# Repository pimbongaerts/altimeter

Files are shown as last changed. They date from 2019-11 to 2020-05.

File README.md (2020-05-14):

# Altimeter_v2

Intervalometer with serial interface based on Mega2560 MCU

*Current application:*

* Intervalometer for photogrammetry surveys (triggering a Canon 5DsR DSLR every second)
* Real-time sensor feedback underwater (through attached OLED display):
  * Levelling and altitude (through 2 x altimeters: [BlueRobotics Ping Sonar](https://bluerobotics.com/store/sensors-sonars-cameras/sonar/ping-sonar-r2-rp/))
  * Read-out USBL communications (through [BluePrint Subsea X150 USBL](https://www.blueprintsubsea.com/pages/product.php?PN=BP00795))
  * Depth and "bottom-depth" based on altitude (through [BlueRobotics Depth Sensor](https://bluerobotics.com/store/sensors-sonars-cameras/sensors/bar30-sensor-r1/))
  * Stopwatch & intervalometer count (triggered by Remora remote)
* Logging synchronized sensor data on SD card

*Features:*

* Real-time clock (RTC) for timekeeping
* SD-card reader to log sensor data
* 4-Channel Optocoupler to trigger camera(s)
* Step-down regulator to run board & DSLR camera off external battery (e.g. from dive propulsion vehicle)
* Supports I2C (3.3V or 5V logic), UART and RS232 sensors
* Connectors for remote controller & I2C or SPI display
* Headers to connect with [Robotdyn MCU-PRO Mega 2560 board](https://robotdyn.com/mcu-pro-mega-2560-atmega2560-16au-usb-ch340c-with-pinheaders-2-lines-pinheaders-pitch-0-1.html), which can be programmed using Arduino IDE
* Fits inside [BlueRobotics 2" watertight enclosure](https://bluerobotics.com/product-category/watertight-enclosures/) (see image below)

## Schematic

[PDF Schematic](altimeter_v2_schematic.pdf)

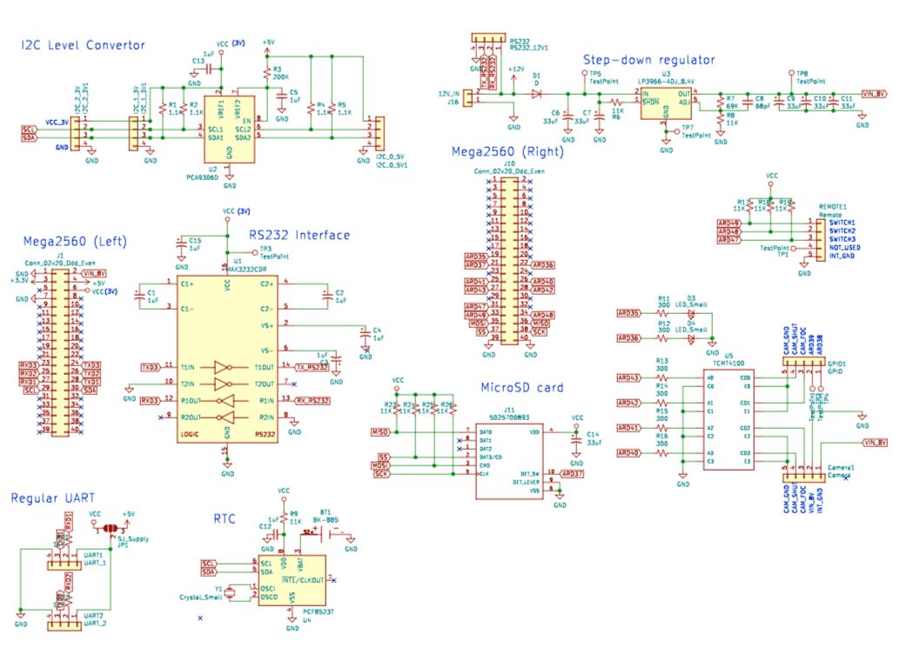
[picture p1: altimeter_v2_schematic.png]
altimeter_photo


* Note: LP3966 on schematic replaced with [TL1963AKTTRG3](https://www.digikey.com/product-detail/en/texas-instruments/TL1963AKTTRG3/296-35958-1-ND/4135050) (has the same footprint)

## Arduino code

[Arduino code](altimeter_v2.ino) (some features are currently commented out)

## PCB Design

[KiCad PCB file](altimeter_v2.kicad_pcb) / [Bill of materials](altimeter_v2_bill.csv)

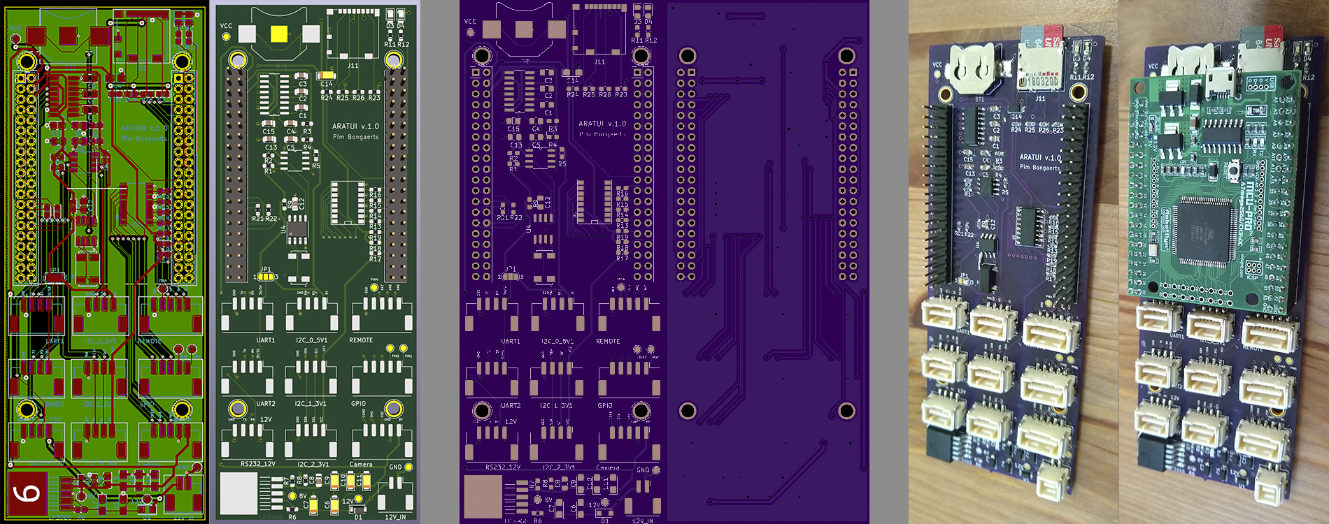
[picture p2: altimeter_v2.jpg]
altimeter_photo


* Note: footprint of the [XC1195CT-ND Crystal](https://www.digikey.com/product-detail/en/ecs-inc/ECS-327-12-5-17X-TR/XC1195CT-ND/827659) turned out to be incorrect, but could easily remedied with direct bridge to RTC pin

## Underwater housing

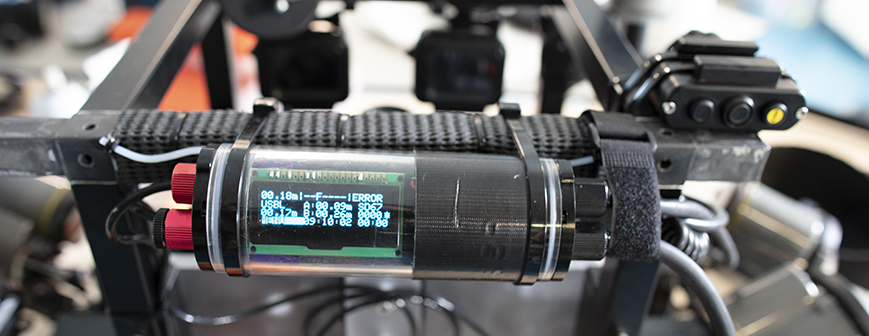
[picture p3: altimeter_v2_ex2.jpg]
altimeter_photo


Image shows board installed in a [BlueRobotics 2" watertight enclosure](https://bluerobotics.com/product-category/watertight-enclosures/), and with a 20x4 OLED display connected. On the left side, there are penetrators for an on/off switch, a [BlueRobotics Depth Sensor](https://bluerobotics.com/store/sensors-sonars-cameras/sensors/bar30-sensor-r1/), and 2 x [BlueRobotics Ping Sonar](https://bluerobotics.com/store/sensors-sonars-cameras/sonar/ping-sonar-r2-rp/) (although on the photo only one connected, hence the "error" on the top-right of the display). On the right side, there is an Ikelite connector to connect with the camera (power and trigger), another Ikelite connector for the 3-button remote (Remora), a penetrator for a cable connecting with the Dive-Xtras Piranha DPV battery, and a penetrator for the cable connecting with the [BluePrint Subsea X150 USBL](https://www.blueprintsubsea.com/pages/product.php?PN=BP00795).

## Final notes

Acknowledging John Atkins for all the design advice! Currently working on next iteration with SAMD51 integrated on the board (no external controller board required).

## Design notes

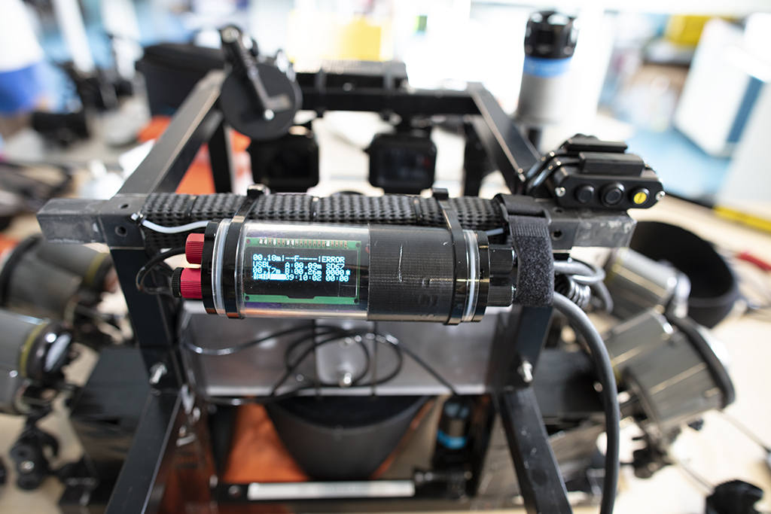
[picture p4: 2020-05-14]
altimeter_v2_ex1.jpg

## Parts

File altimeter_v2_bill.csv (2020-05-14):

BT1 | BK-885 | BAT_BK-885 | 3.17mm
C1 | 1uF | Capacitor_SMD:C_0805_2012Metric_Pad1.15x1.40mm_HandSolder | ~
C12 | 1uF | Capacitor_SMD:C_0805_2012Metric_Pad1.15x1.40mm_HandSolder | ~
C13 | 1uF | Capacitor_SMD:C_0805_2012Metric_Pad1.15x1.40mm_HandSolder | ~
C15 | 1uF | Capacitor_SMD:C_0805_2012Metric_Pad1.15x1.40mm_HandSolder | ~
C2 | 1uF | Capacitor_SMD:C_0805_2012Metric_Pad1.15x1.40mm_HandSolder | ~
C3 | 1uF | Capacitor_SMD:C_0805_2012Metric_Pad1.15x1.40mm_HandSolder | ~
C4 | 1uF | Capacitor_SMD:C_0805_2012Metric_Pad1.15x1.40mm_HandSolder | ~
C5 | 1uF | Capacitor_SMD:C_0805_2012Metric_Pad1.15x1.40mm_HandSolder | ~
C8 | 68pF | Capacitor_SMD:C_0805_2012Metric_Pad1.15x1.40mm_HandSolder | ~
C10 | 33uF | Capacitor_Tantalum_SMD:CP_EIA-3216-10_Kemet-I_Pad1.58x1.35mm_HandSolder | ~
C11 | 33uF | Capacitor_Tantalum_SMD:CP_EIA-3216-10_Kemet-I_Pad1.58x1.35mm_HandSolder | ~
C14 | 33uF | Capacitor_Tantalum_SMD:CP_EIA-3216-10_Kemet-I_Pad1.58x1.35mm_HandSolder | ~
C6 | 33uF | Capacitor_Tantalum_SMD:CP_EIA-3216-10_Kemet-I_Pad1.58x1.35mm_HandSolder | ~
C7 | 33uF | Capacitor_Tantalum_SMD:CP_EIA-3216-10_Kemet-I_Pad1.58x1.35mm_HandSolder | ~
C9 | 33uF | Capacitor_Tantalum_SMD:CP_EIA-3216-10_Kemet-I_Pad1.58x1.35mm_HandSolder | ~
J11 | 5025700893 | Connector_Card:microSD_HC_Molex_104031-0811 | Molex
J16 | 12V_IN | Connector_Molex:Molex_CLIK-Mate_502382-0270_1x02-1MP_P1.25mm_Vertical | ~
J17 | 12V_OUT | Connector_Molex:Molex_CLIK-Mate_502382-0270_1x02-1MP_P1.25mm_Vertical | ~
J9 | RS232_USBL | Connector_Molex:Molex_CLIK-Mate_502382-0270_1x02-1MP_P1.25mm_Vertical | ~
J3 | UART_1 | Connector_Molex:Molex_CLIK-Mate_502443-0470_1x04-1MP_P2.00mm_Vertical | ~
J4 | UART_2 | Connector_Molex:Molex_CLIK-Mate_502443-0470_1x04-1MP_P2.00mm_Vertical | ~
J5 | I2C_0_5V | Connector_Molex:Molex_CLIK-Mate_502443-0470_1x04-1MP_P2.00mm_Vertical | ~
J6 | I2C_1_3V | Connector_Molex:Molex_CLIK-Mate_502443-0470_1x04-1MP_P2.00mm_Vertical | ~
J8 | I2C_2_3V | Connector_Molex:Molex_CLIK-Mate_502443-0470_1x04-1MP_P2.00mm_Vertical | ~
J13 | GPIO | Connector_Molex:Molex_CLIK-Mate_502443-0570_1x05-1MP_P2.00mm_Vertical | ~
J14 | Cam1 | Connector_Molex:Molex_CLIK-Mate_502443-0570_1x05-1MP_P2.00mm_Vertical | ~
J15 | Remote | Connector_Molex:Molex_CLIK-Mate_502443-0570_1x05-1MP_P2.00mm_Vertical | ~
J1 | Conn_02x20_Odd_Even | Connector_PinHeader_2.54mm:PinHeader_2x20_P2.54mm_Vertical | ~
J10 | Conn_02x20_Odd_Even | Connector_PinHeader_2.54mm:PinHeader_2x20_P2.54mm_Vertical | ~
D1 | D | Diode_SMD:D_SOD-123F | ~
Y1 | Crystal_Small | ECS-.327-12:XTAL_ECS-.327-12.5-17X-TR | ~
JP1 | SJ_Supply | Jumper:SolderJumper-3_P1.3mm_Open_RoundedPad1.0x1.5mm_NumberLabels | ~
D3 | LED_Small | LED_SMD:LED_0805_2012Metric_Pad1.15x1.40mm_HandSolder | ~
D4 | LED_Small | LED_SMD:LED_0805_2012Metric_Pad1.15x1.40mm_HandSolder | ~
U3 | LP3966-ADJ_8.4V | LP3966ESX-ADJ_NOPB:TO170P1435X457-5N | http://www.ti.com/lit/ds/symlink/lp3966.pdf
U1 | MAX3232CDR | MAX3232CDR:SOIC127P600X175-16N | http://www.ti.com/lit/ds/symlink/max232.pdf
U4 | PCF8523T | Package_SO:SOIC-8_3.9x4.9mm_P1.27mm | https://www.nxp.com/docs/en/data-sheet/PCF8523.pdf
U2 | PCA9306D | PCA9306D_118:SOIC127P600X175-8N | http://www.ti.com/lit/ds/symlink/pca9306.pdf
R1 | 1.1K | Resistor_SMD:R_0603_1608Metric_Pad1.05x0.95mm_HandSolder | ~
R11 | 300 | Resistor_SMD:R_0603_1608Metric_Pad1.05x0.95mm_HandSolder | ~
R12 | 300 | Resistor_SMD:R_0603_1608Metric_Pad1.05x0.95mm_HandSolder | ~
R13 | 300 | Resistor_SMD:R_0603_1608Metric_Pad1.05x0.95mm_HandSolder | ~
R14 | 300 | Resistor_SMD:R_0603_1608Metric_Pad1.05x0.95mm_HandSolder | ~
R15 | 300 | Resistor_SMD:R_0603_1608Metric_Pad1.05x0.95mm_HandSolder | ~
R16 | 300 | Resistor_SMD:R_0603_1608Metric_Pad1.05x0.95mm_HandSolder | ~
R17 | 11K | Resistor_SMD:R_0603_1608Metric_Pad1.05x0.95mm_HandSolder | ~
R18 | 11K | Resistor_SMD:R_0603_1608Metric_Pad1.05x0.95mm_HandSolder | ~
R19 | 11K | Resistor_SMD:R_0603_1608Metric_Pad1.05x0.95mm_HandSolder | ~
R2 | 1.1K | Resistor_SMD:R_0603_1608Metric_Pad1.05x0.95mm_HandSolder | ~
R21 | 11K | Resistor_SMD:R_0603_1608Metric_Pad1.05x0.95mm_HandSolder | ~
R22 | 11K | Resistor_SMD:R_0603_1608Metric_Pad1.05x0.95mm_HandSolder | ~
R23 | 11K | Resistor_SMD:R_0603_1608Metric_Pad1.05x0.95mm_HandSolder | ~
R24 | 11K | Resistor_SMD:R_0603_1608Metric_Pad1.05x0.95mm_HandSolder | ~
R25 | 11K | Resistor_SMD:R_0603_1608Metric_Pad1.05x0.95mm_HandSolder | ~
R26 | 11K | Resistor_SMD:R_0603_1608Metric_Pad1.05x0.95mm_HandSolder | ~
R3 | 200K | Resistor_SMD:R_0603_1608Metric_Pad1.05x0.95mm_HandSolder | ~
R4 | 1.1K | Resistor_SMD:R_0603_1608Metric_Pad1.05x0.95mm_HandSolder | ~
R5 | 1.1K | Resistor_SMD:R_0603_1608Metric_Pad1.05x0.95mm_HandSolder | ~
R6 | 11K | Resistor_SMD:R_0603_1608Metric_Pad1.05x0.95mm_HandSolder | ~
R7 | 69K | Resistor_SMD:R_0603_1608Metric_Pad1.05x0.95mm_HandSolder | ~
R8 | 11K | Resistor_SMD:R_0603_1608Metric_Pad1.05x0.95mm_HandSolder | ~
R9 | 11K | Resistor_SMD:R_0603_1608Metric_Pad1.05x0.95mm_HandSolder | ~
U5 | TCMT4100 | TCMT4100:SOP-16

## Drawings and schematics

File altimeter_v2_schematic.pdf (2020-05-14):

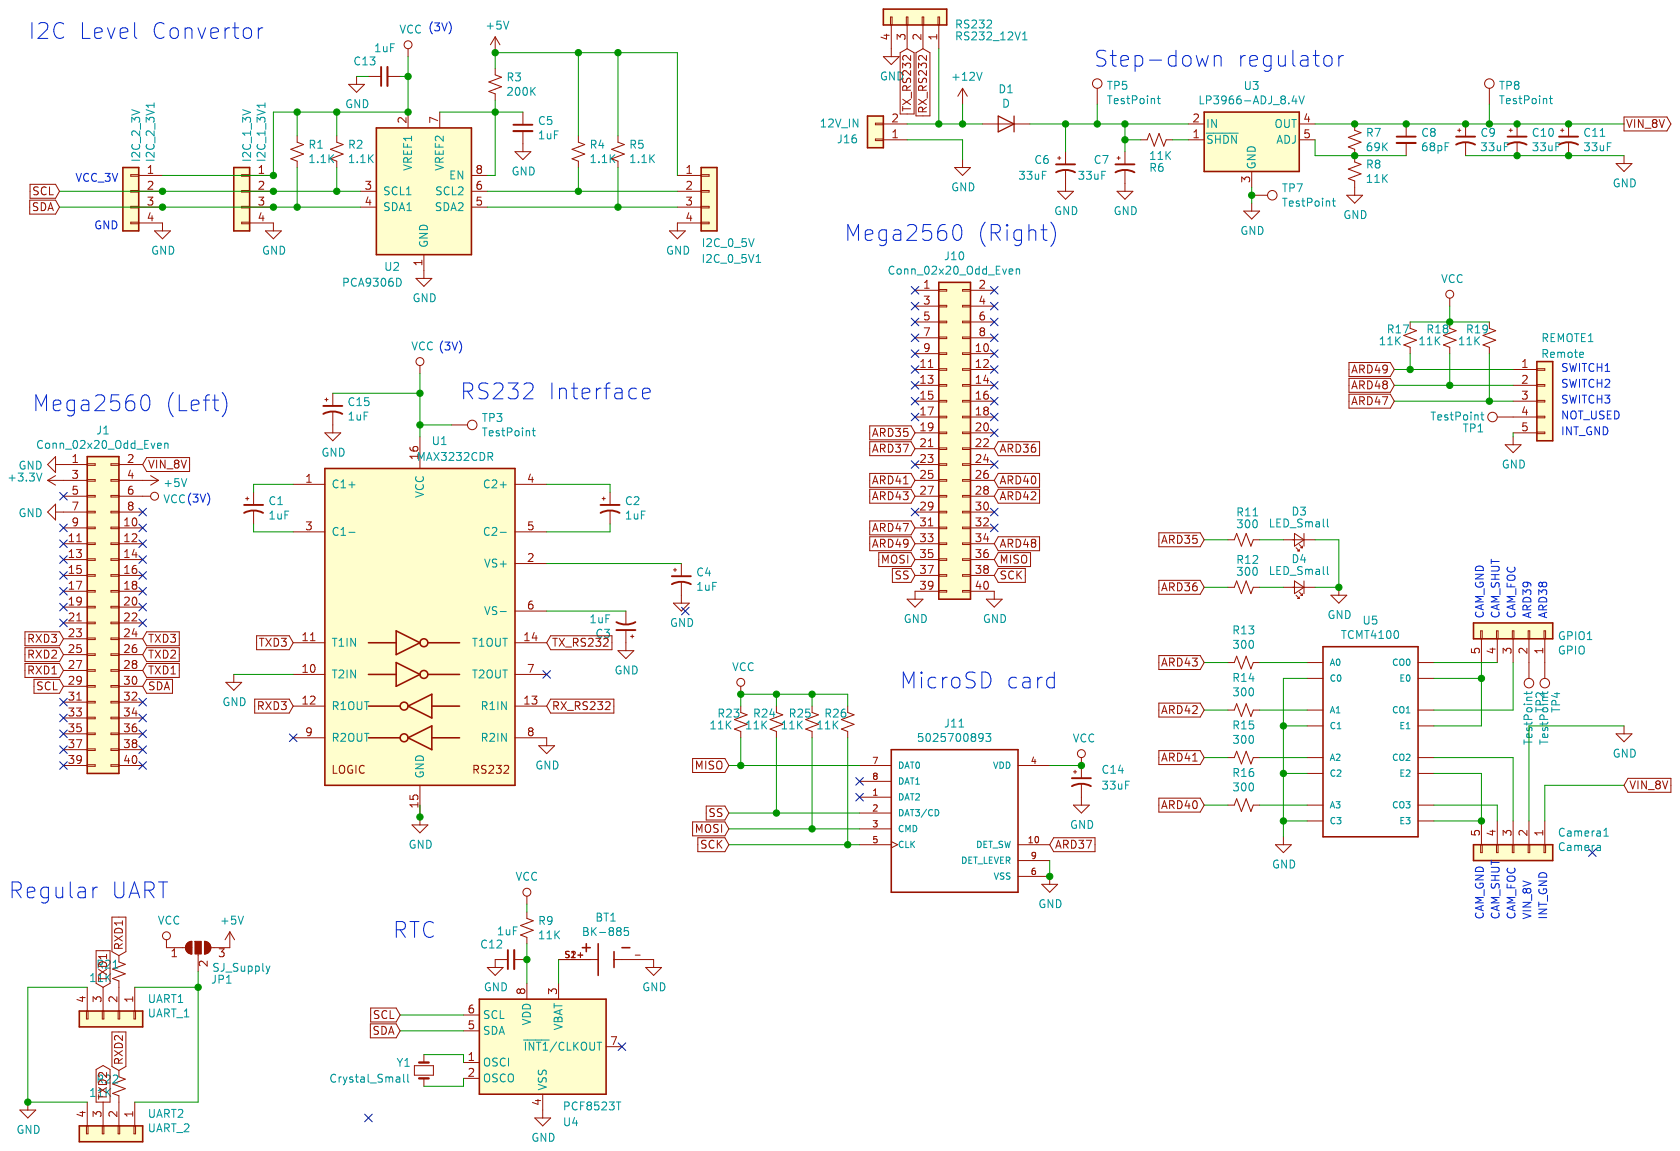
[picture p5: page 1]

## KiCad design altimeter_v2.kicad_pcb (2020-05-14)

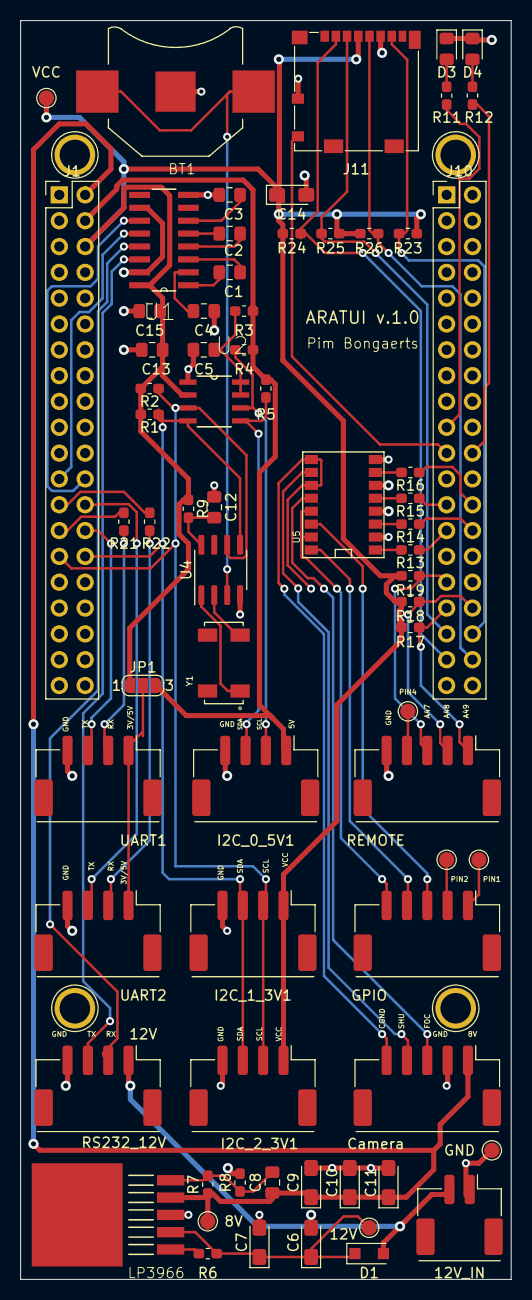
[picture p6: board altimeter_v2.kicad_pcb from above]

Board: 2 copper layers, 48.3 x 123.8 mm, 70 parts (0 on the bottom side), 63 nets.

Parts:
8V, 12V: TestPoint; TestPoint_Pad_D1.5mm
12V_IN: 12V_IN; Molex_CLIK-Mate_502443-0270_1x02-1MP_P2.00mm_Vertical
BT1: BK-885; BAT_BK-885
C1, C2, C3, C4, C5, C12, C13, C15: 1uF; C_0805_2012Metric_Pad1.15x1.40mm_HandSolder
C6, C7, C9, C10, C11, C14: 33uF; CP_EIA-3216-10_Kemet-I_Pad1.58x1.35mm_HandSolder
C8: 68pF; C_0805_2012Metric_Pad1.15x1.40mm_HandSolder
Camera: Camera; Molex_CLIK-Mate_502443-0570_1x05-1MP_P2.00mm_Vertical
D1: D; D_SOD-123F
D3, D4: LED_Small; LED_0805_2012Metric_Pad1.15x1.40mm_HandSolder
GND: TestPoint; TestPoint_Pad_D1.5mm
GPIO: GPIO; Molex_CLIK-Mate_502443-0570_1x05-1MP_P2.00mm_Vertical
I2C_0_5V1: I2C_0_5V; Molex_CLIK-Mate_502443-0470_1x04-1MP_P2.00mm_Vertical
I2C_1_3V1: I2C_1_3V; Molex_CLIK-Mate_502443-0470_1x04-1MP_P2.00mm_Vertical
I2C_2_3V1: I2C_2_3V; Molex_CLIK-Mate_502443-0470_1x04-1MP_P2.00mm_Vertical
J1, J10: Conn_02x20_Odd_Even; PinHeader_2x20_P2.54mm_Vertical
J11: 5025700893; microSD_HC_Molex_104031-0811
JP1: SJ_Supply; SolderJumper-3_P1.3mm_Open_RoundedPad1.0x1.5mm_NumberLabels
LP3966: LP3966-ADJ_8.4V; TO170P1435X457-5N
PIN1, PIN2, PIN4: TestPoint; TestPoint_Pad_D1.5mm
R1, R2, R4, R5: 1.1K; R_0603_1608Metric_Pad1.05x0.95mm_HandSolder
R3: 200K; R_0603_1608Metric_Pad1.05x0.95mm_HandSolder
R6, R8, R9, R17, R18, R19, R21, R22, R23, R24, R25, R26: 11K; R_0603_1608Metric_Pad1.05x0.95mm_HandSolder
R7: 69K; R_0603_1608Metric_Pad1.05x0.95mm_HandSolder
R11, R12, R13, R14, R15, R16: 300; R_0603_1608Metric_Pad1.05x0.95mm_HandSolder
REMOTE: Remote; Molex_CLIK-Mate_502443-0570_1x05-1MP_P2.00mm_Vertical
RS232_12V: RS232; Molex_CLIK-Mate_502443-0470_1x04-1MP_P2.00mm_Vertical
U1: MAX3232CDR; SOIC127P600X175-16N
U2: PCA9306D; SOIC127P600X175-8N
U4: PCF8523T; SOIC-8_3.9x4.9mm_P1.27mm
U5: TCMT4100; SOP-16
UART1: UART_1; Molex_CLIK-Mate_502443-0470_1x04-1MP_P2.00mm_Vertical
UART2: UART_2; Molex_CLIK-Mate_502443-0470_1x04-1MP_P2.00mm_Vertical
VCC: TestPoint; TestPoint_Pad_D1.5mm
Y1: Crystal_Small; XTAL_ECS-.327-12.5-17X-TR

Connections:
+5V: I2C_0_5V1.1, J1.4, JP1.3, R3.1, R4.1, R5.1
+12V: 12V_IN.2, D1.2, RS232_12V.1
ARD35: J10.19, R11.2
ARD36: J10.22, R12.2
ARD37: J10.21, J11.10
ARD40: J10.26, R16.2
ARD41: J10.25, R15.2
ARD42: J10.28, R14.2
ARD43: J10.27, R13.2
ARD47: J10.31, R19.1, REMOTE.3
ARD48: J10.34, R18.1, REMOTE.2
ARD49: J10.33, R17.1, REMOTE.1
GND: 12V_IN.1, BT1.-, C3.1, C4.2, C5.2, C6.2, C7.2, C9.2, C10.2, C11.2, C12.1, C13.1, C14.2, C15.2, Camera.2, D3.1, D4.1, GND.1, I2C_0_5V1.4, I2C_1_3V1.4, I2C_2_3V1.4, J1.1, J1.7, J10.39, J10.40, J11.6, J11.9, LP3966.3, R8.2, REMOTE.5, RS232_12V.4, U1.8, U1.10, U1.15, U2.1, U4.4, U5.2, U5.4, U5.6, U5.8, UART1.4, UART2.4
MISO: J10.36, J11.7, R23.1
MOSI: J10.35, J11.3, R25.1
unnamed: BT1.S1+, BT1.S2+, U4.3
unnamed: C1.1, U1.1
unnamed: C1.2, U1.3
unnamed: C2.1, U1.4
unnamed: C2.2, U1.5
unnamed: C3.2, U1.6
unnamed: C4.1, U1.2
unnamed: C5.1, R3.2, U2.7, U2.8
unnamed: 12V.1, C6.1, C7.1, D1.1, LP3966.2, R6.2
unnamed: C8.2, LP3966.5, R7.2, R8.1
unnamed: C12.2, R9.2, U4.8
unnamed: Camera.3, U5.12
unnamed: Camera.4, U5.10
unnamed: Camera.5, U5.9, U5.11
unnamed: D3.2, R11.1
unnamed: D4.2, R12.1
unnamed: GPIO.1, PIN1.1
unnamed: GPIO.2, PIN2.1
unnamed: GPIO.3, U5.14
unnamed: GPIO.4, U5.16
unnamed: GPIO.5, U5.13, U5.15
unnamed: I2C_0_5V1.2, R4.2, U2.6
unnamed: I2C_0_5V1.3, R5.2, U2.5
unnamed: JP1.2, UART1.1, UART2.1
unnamed: LP3966.1, R6.1
unnamed: R13.1, U5.1
unnamed: R14.1, U5.3
unnamed: R15.1, U5.5
unnamed: R16.1, U5.7
unnamed: R21.2, UART1.2
unnamed: R22.2, UART2.2
unnamed: PIN4.1, REMOTE.4
unnamed: U4.1, Y1.1
unnamed: U4.2, Y1.2
RXD1: J1.27, R21.1
RXD2: J1.25, R22.1
RXD3: J1.23, U1.12
RX_RS232: RS232_12V.2, U1.13
SCK: J10.38, J11.5, R26.1
SCL: I2C_1_3V1.2, I2C_2_3V1.2, J1.29, R2.2, U2.3, U4.6
SDA: I2C_1_3V1.3, I2C_2_3V1.3, J1.30, R1.2, U2.4, U4.5
SS: J10.37, J11.2, R24.1
TXD1: J1.28, UART1.3
TXD2: J1.26, UART2.3
TXD3: J1.24, U1.11
TX_RS232: RS232_12V.3, U1.14
VCC: C13.2, C14.1, C15.1, I2C_1_3V1.1, I2C_2_3V1.1, J1.6, J11.4, JP1.1, R1.1, R2.1, R9.1, R17.2, R18.2, R19.2, R23.2, R24.2, R25.2, R26.2, U1.16, U2.2, VCC.1
VIN_8V: 8V.1, C8.1, C9.1, C10.1, C11.1, Camera.1, J1.2, LP3966.4, R7.1

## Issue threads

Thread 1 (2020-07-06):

### ISSUE TITLE
Specifications: 3-button remote (Remora)

### ISSUE THREAD

**Issue by CexyNature** [pimbongaerts/altimeter#1]
Pim awesome project!
I was wondering if the 3-button remote you mention in README is a custom made product? and if these are push buttons?

> On the right side, there is an Ikelite connector to connect with the camera (power and trigger), another Ikelite connector for the 3-button remote (Remora), ...

Thanks, I look forward to the next iteration.

**Comment by pimbongaerts** [comment]
Thanks Cesar! It was a product that Backscatter used to carry (maybe produce?) - but not anymore unfortunately, and cannot really find it anywhere on the web. It has 3 push buttons and an Ikelite connector.

**Comment by CexyNature** [comment]
Thanks! It is super great idea to have a keypad with buttons. I have been looking other options like the [Blue Robotics switch](https://bluerobotics.com/store/comm-control-power/switch/switch-10-5a-r1/) or other underwater rated buttons (but these cannot be mounted in M10 holes). 

Having a keypad with three button and just one cable penetrator is an amazing setup!

Many thanks! 😃

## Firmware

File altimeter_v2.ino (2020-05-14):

/* Diving Altimeter
-----------------------------------------------------
 
Title: Aratui TEST

Description: 
-------------------------------*/
// Libraries
#include <Wire.h>                          // I2C Communication
#include <Adafruit_GFX.h>                  // Graphics for OLED
#include <Adafruit_SSD1305.h>              // OLED
#include <RTClib.h>                        // Real-time clock
#include <SPI.h>                           // SPI for SD card
#include <SD.h>                            // SD card reader
#include <MS5837.h>                        // Bar30 depth sensor
#include <ping1d.h>                        // Ping sonar / altimeter
#include <Bounce2.h>                       // Debouncing remote buttons

// Constants
#define OLED_COLS 20
#define OLED_ROWS 4
#define FLUID_DENSITY 1029
#define BUTTON_PRESS_DELAY 300
#define NOT_RESPONSIVE -999
#define NOT_RUNNING -999
#define INTERVAL 1000
#define SHUTTER_DELAY 300

// #define PIN_LED_GREEN 35               // Removed from board
// #define PIN_LED_RED 36                 // Removed from board
#define PIN_CAM_SHUTTER 40
#define PIN_CAM_FOCUS 41
#define PIN_BUTTON1 47
#define PIN_BUTTON2 48
#define PIN_BUTTON3 49
#define PIN_CHIPSELECT 53
#define OLED_RESET 70

// Global objects
File logfile;
Adafruit_SSD1305 display(OLED_RESET);
RTC_PCF8523 rtc;
MS5837 depth_sensor;
static Ping1D ping_left { Serial1 };
static Ping1D ping_right { Serial2 };

// Global objects
unsigned long stopwatch_stored_millis;
unsigned long stopwatch_start_millis;
unsigned long stopwatch_millis;
unsigned long previous_millis = 0;
int stopwatch_min = 0;
int stopwatch_sec = 0;
bool stopwatch_running = false;
bool delayed_start_stopwatch = false;
bool delayed_single_trigger_camera = false;
float ping_altitude_left = NOT_RESPONSIVE;
float ping_altitude_conf_left = NOT_RESPONSIVE;
float ping_altitude_right = NOT_RESPONSIVE;
float ping_altitude_conf_right = NOT_RESPONSIVE;
float mean_altitude = NOT_RESPONSIVE;
float bar30_depth = NOT_RESPONSIVE;
float extrapolated_depth = NOT_RESPONSIVE;
float usbl = NOT_RESPONSIVE;
int rtc_year = NOT_RESPONSIVE;
int rtc_month = NOT_RESPONSIVE;
int rtc_day = NOT_RESPONSIVE;
int rtc_hour = NOT_RESPONSIVE;
int rtc_min = NOT_RESPONSIVE;
int rtc_sec = NOT_RESPONSIVE;
unsigned long rtc_unixtime = NOT_RESPONSIVE;
int sd_file_number = NOT_RESPONSIVE;
int progress_update = -1;
int intervalometer_number = NOT_RUNNING;
int total_trigger_number = 0;
int current_menu = 0;
byte customBackslash[8] = {
  0b00000,
  0b10000,
  0b01000,
  0b00100,
  0b00010,
  0b00001,
  0b00000,
  0b00000
};

void init_pins() {
  // Initialize pins
  pinMode(PIN_BUTTON1, INPUT);
  pinMode(PIN_BUTTON2, INPUT);
  pinMode(PIN_BUTTON3, INPUT);
  pinMode(PIN_CAM_SHUTTER, OUTPUT);
  pinMode(PIN_CAM_FOCUS, OUTPUT);
}

// Initialize LCD screen
void init_oled() {
  display.begin();
  display.clearDisplay();
  display.display();
  display.setTextSize(1);
  display.setTextColor(WHITE);
  display.setCursor(0,0);
  display.println("DEEPCAT");
  display.display();
}

// Initialize Real-Time Clock
void init_rtc() {
  if (! rtc.begin()) {
    rtc_hour = NOT_RESPONSIVE;
  } else {
    // SET TIME TO CURRENT COMPUTER TIME
    // rtc.adjust(DateTime(F(__DATE__), F(__TIME__)));
    // Update current date/time
    get_rtc_time();
  }
}

void get_rtc_time() {
  DateTime now = rtc.now();
  rtc_year = now.year();
  rtc_month = now.month();
  rtc_day = now.day();
  rtc_hour = now.hour();
  rtc_min = now.minute();
  rtc_sec = now.second();
  rtc_unixtime = now.unixtime();
}

// Initialize SD card
void init_sdcard() {
  display.clearDisplay();
  pinMode(PIN_CHIPSELECT, OUTPUT);
  if (!SD.begin(PIN_CHIPSELECT)) {
    sd_file_number = NOT_RESPONSIVE;
  }
  // create a new file
  char filename[] = "ARAT0000.CSV";
  for (uint8_t i = 0; i < 10000; i++) {
    filename[4] = '0' + ((i / 1000) % 10);
    filename[5] = '0' + ((i / 100) % 10);
    filename[6] = '0' + ((i / 10) % 10);
    filename[7] = '0' + (i % 10);
    if (! SD.exists(filename)) {
      // only open a new file if it doesn't exist
      logfile = SD.open(filename, FILE_WRITE);
      sd_file_number = i;
      break;  // leave the loop!
    }
  }
  if (! logfile) {
    sd_file_number = NOT_RESPONSIVE;
  } else {
    // print logfile header
    logfile.println(F("date,time,unixtime,depth,left_altitude,left_altitude_confidence,right_altitude,right_altitude_confidence,mean_altitude,extrapolated_depth,stopwatch_time,intervalometer_no,total_trigger_number,millis"));
  }
}

void init_depth_sensor() {
  // Initialize pressure depth_sensor (true if initialization was successful)
  Wire.begin();
  while (!depth_sensor.init()) {
    delay(1000);
  }
  depth_sensor.setModel(MS5837::MS5837_30BA);
  depth_sensor.setFluidDensity(FLUID_DENSITY);
  get_bar30_depth();
}

// Obtain depth measurement
void get_bar30_depth() {
  depth_sensor.read();
  bar30_depth = depth_sensor.depth(); 
}

// Initialize left altimeter
void init_sonar_left() {
  Serial1.begin(9600);
  int attempts = 0;
  while (!ping_left.initialize()) { 
    if (attempts > 3) { break; }
    attempts++;
    delay(200);
  }
  ping_get_altitude_left();
}

// Initialize right altimeter
void init_sonar_right() {
  Serial2.begin(115200);
  int attempts = 0;
  while (!ping_right.initialize()) { 
    if (attempts > 10) { break; }
    attempts++;
    delay(500);
  }
  ping_left.set_ping_enable(true); // to remove
  ping_get_altitude_right();
}

// Initialize right altimeter
void init_usbl() {
  Serial3.begin(115200);
  if (Serial3.available() <= 0 ) {
    usbl = NOT_RESPONSIVE;
  }
}

// Obtain altitude measurement
void ping_get_altitude_left() {
    // ping_left.set_ping_enable(true);
    if (ping_left.update()) {
        ping_altitude_left = (float)ping_left.distance() / 1000;
        ping_altitude_conf_left = ping_left.confidence();
    } else {
        ping_altitude_left = NOT_RESPONSIVE;
        ping_altitude_conf_left = 0;
    }
    // ping_left.set_ping_enable(false);
}

// Obtain altitude measurement
void ping_get_altitude_right() {
    // ping_right.set_ping_enable(true);
    if (ping_right.update()) {
        ping_altitude_right = (float)ping_right.distance() / 1000;
        ping_altitude_conf_right = ping_right.confidence();
    } else {
        ping_altitude_right = NOT_RESPONSIVE;
        ping_altitude_conf_right = 0;
    }
    // ping_right.set_ping_enable(false);
}
// Obtain USBL information
void usbl_get_data() {
  if (Serial3.available() > 0) {
    usbl = 1;
  } else {
    usbl = NOT_RESPONSIVE;
  }
}

// Print depth/altitude to LCD
void oled_print_6char(float number) {
  if (number == NOT_RESPONSIVE) {
    display.print(F("-N/A- "));
  } else if (number >= 1000) {
    display.print(F("100+m "));
  } else if (number > 100) {
    display.print((int) number);
    display.print(F("m "));
  } else if (number > 10) {
    display.print(number);
    display.print(F("m"));
  } else if (number > 0) {
    display.print(F("0"));
    display.print(number);
    display.print(F("m"));
  } else if (number < 0) {
    display.print(F("-NEG- "));
  } else {
    display.print(F("ERROR "));
  }
}

// Print time to OLED
void oled_print_rtc_time(int number1, int number2, int number3) {
  if (number1 == NOT_RESPONSIVE) {
    display.print(F("-N/A-"));
  } else {
    if (number1 < 10) { display.print(F("0")); }
    display.print(number1);
    display.print(F(":"));
    if (number2 < 10) { display.print(F("0")); }
    display.print(number2);
    display.print(F(":"));
    if (number3 < 10) { display.print(F("0")); }
    display.print(number3);
  }
}

// Print time to OLED
void oled_print_time(int number1, int number2) {
  if (number1 == NOT_RESPONSIVE) {
    display.print(F("-N/A-"));
  } else {
    if (number1 < 10) { display.print(F("0")); }
    display.print(number1);
    display.print(F(":"));
    if (number2 < 10) { display.print(F("0")); }
    display.print(number2);
  }
}

// Print SD card filenumber to OLED
void oled_print_sd_card() {
  if (sd_file_number == NOT_RESPONSIVE) {
    display.print(F("NOSD"));
    return;
  } else if (sd_file_number < 10) {
    display.print(F("SD0"));
  } else if (sd_file_number < 100) {
    display.print(F("SD"));
  } else if (sd_file_number < 1000) {
    display.print(F("0"));
  }
  display.print(sd_file_number);
}

// Print photo number to OLED
void oled_print_total_trigger_number() {
  if (total_trigger_number < 10) {
    display.print(F("000"));
  } else if (total_trigger_number < 100) {
    display.print(F("00"));
  } else if (total_trigger_number < 1000) {
    display.print(F("0"));
  }
  display.print(total_trigger_number);
}

// Get mean altitude
void get_mean_altitude() {
  if ((ping_altitude_left != NOT_RESPONSIVE) && (ping_altitude_right != NOT_RESPONSIVE)) {
    mean_altitude = (ping_altitude_left + ping_altitude_right) / 2;
  } else if (ping_altitude_left != NOT_RESPONSIVE) {
    mean_altitude = ping_altitude_left;
  } else if (ping_altitude_right != NOT_RESPONSIVE) {
    mean_altitude = ping_altitude_right;
  } else {
    mean_altitude = NOT_RESPONSIVE;
  }
}

// Get extrapolated depth
void get_extrapolated_depth() {
  if (mean_altitude != NOT_RESPONSIVE) {
    extrapolated_depth = bar30_depth + mean_altitude;
  } else {
    extrapolated_depth = NOT_RESPONSIVE;
  }
}

// Get progress update character
void oled_print_progress_character() {
  display.setCursor(122, 17);
  if (intervalometer_number == NOT_RUNNING) {
    if (progress_update == 0) { 
      display.print(F("*")); 
    } else {
      display.print(F("."));
      progress_update = -1;
    }
  } else {
    if (progress_update == 0) { 
      display.print(F("|")); 
    } else if (progress_update == 1) { 
      display.print(F("/")); 
    } else if (progress_update == 2) { 
      display.print(F("-")); 
    } else {
      display.print(F("\\"));
      progress_update = -1;
    }
  }
}

// Get progress update character
void oled_print_button_character() {
  display.setCursor(122,17);
  display.print(F("B"));
  display.display();
}
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

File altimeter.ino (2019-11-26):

/* Diving Altimeter
-----------------------------------------------------
 
Title: Diving Altimeter

Description: Displays (LCD) and logs (SD card) depth 
and altitude. Designed for Arduino Uno with Adafruit
Datalogger Shield and BlueRobotics Ping & Bar30 
sensors.

-------------------------------*/
// Libraries
#include <SPI.h>
#include <SD.h>
#include <Wire.h>
#include <MS5837.h>
#include <hd44780.h>
#include <hd44780ioClass/hd44780_I2Cexp.h>
#include "RTClib.h"
#include "ping1d.h"
#include "SoftwareSerial.h"

// Constants
#define chipSelect 8
#define arduinoRxPin 9
#define arduinoTxPin 10
#define LCD_COLS 20
#define LCD_ROWS 4
#define FLUID_DENSITY 1029

// Global objects/variables
File logfile;
SoftwareSerial pingSerial = SoftwareSerial(arduinoRxPin, arduinoTxPin);
hd44780_I2Cexp lcd;
MS5837 depth_sensor;
RTC_PCF8523 rtc;
static Ping1D ping { pingSerial };

// Initialize LCD screen
void init_lcd() {
  int lcd_status;
  lcd_status = lcd.begin(LCD_COLS, LCD_ROWS);
  if(lcd_status) {
    // // non-zero status means begin() failed
    lcd_status = -lcd_status; // convert negative status value to positive number
    hd44780::fatalError(lcd_status); // error code using the onboard LED if possible & exit
  }
  // Clear screen
  lcd.clear();
}

// Initialize Real-Time Clock
void init_rtc() {
  lcd.setCursor(0, 0);
  if (! rtc.begin()) {
    lcd.print(F("Real-time clock...NO"));
  }
  // Set time to current computer time (at compile)
  rtc.adjust(DateTime(F(__DATE__), F(__TIME__)));
  lcd.print(F("Real-time clock...OK"));
}

// Initialize depth sensor
void init_depth_sensor() {
  lcd.setCursor(0, 1);
  Wire.begin();
  // Initialize pressure depth_sensor (true if initialization was successful)
  while (!depth_sensor.init()) {
    lcd.print(F("Depth sensor...   NO"));
    delay(3000);
  }
  depth_sensor.setModel(MS5837::MS5837_30BA);
  depth_sensor.setFluidDensity(FLUID_DENSITY);
  lcd.print(F("Depth sensor...   OK"));
}

// Initialize altimeter
void init_sonar() {
  pingSerial.begin(9600);
  while (!ping.initialize()) {
    lcd.print(F("Sonar...          NO"));
    delay(3000);
  }
  lcd.setCursor(0, 2);
  lcd.print(F("Sonar...          OK"));
}

// Initialize SD card
void init_sdcard() {
  lcd.setCursor(0, 3);
  pinMode(chipSelect, OUTPUT);
  if (!SD.begin(chipSelect)) {
    lcd.print(F("SD card...        NO"));
  }
  // create a new file
  char filename[] = "LOGGER00.CSV";
  for (uint8_t i = 0; i < 100; i++) {
    filename[6] = i/10 + '0';
    filename[7] = i%10 + '0';
    if (! SD.exists(filename)) {
      // only open a new file if it doesn't exist
      logfile = SD.open(filename, FILE_WRITE);
      break;  // leave the loop!
    }
  }
  if (! logfile) {
    lcd.print("SD card...        NO");
  } else {
    // print logfile header
    logfile.println(F("date,time,unixtime,depth,altitude,confidence,bottom_depth"));
    lcd.print(F("SD card: "));
    lcd.print(filename);
  }
}

// Update time on LCD
void lcd_update_time(DateTime now) {
  lcd.setCursor(12, 3);
  lcd.print(F("      "));
  lcd.setCursor(12, 3);
  if (now.hour() < 10) {
    lcd.print(F(" "));
  }
  lcd.print(now.hour(), DEC);
  lcd.setCursor(14, 3);
  lcd.print(F(":"));
  lcd.setCursor(15, 3);
  if (now.minute() < 10) {
    lcd.print(F("0"));
  }
  lcd.print(now.minute(), DEC);
  lcd.setCursor(17, 3);
  lcd.print(F(":"));
  lcd.setCursor(18, 3);
  if (now.second() < 10) {
    lcd.print(F("0"));
  }
  lcd.print(now.second(), DEC);
}

// Update sensor readings on LCD
void lcd_update_sensors(float depth, float altitude, float confidence, 
                        float bottom_depth, float voltage) {
  int conf_int;
  // Depth
  lcd.setCursor(0, 0);
  lcd.print(F("DPT:"));
  if (depth < 10.0) {
    lcd.print(F(" "));
  }
  lcd.print(depth);
  lcd.print(F("m"));
  // Ping voltage
  lcd.setCursor(15, 0);
  lcd.print(voltage);
  lcd.setCursor(19, 0);
  lcd.print(F("V"));
  // Altitude
  lcd.setCursor(0, 1);
  lcd.print(F("ALT:"));
  if (altitude < 10.0) {
    lcd.print(F(" "));
  }
  lcd.print(altitude);
  lcd.print(F("m"));
  // Altitude confidence
  lcd.setCursor(15, 1);
  lcd.print(F("("));
  conf_int = (int) confidence;
  lcd.print(conf_int);
  lcd.print(F(")   "));
  // Bottom
  lcd.setCursor(0, 3);
  lcd.print(F("BOT:"));
  if (bottom_depth < 10.0) {
    lcd.print(F(" "));
  }
  lcd.print(bottom_depth);
  lcd.print(F("m"));
}
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

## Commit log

2019-11-26 Added Arduino script
2020-05-14 Added files for Altimeter v2
    [altimeter_v2.kicad_pcb, altimeter_v2_bill.csv]
